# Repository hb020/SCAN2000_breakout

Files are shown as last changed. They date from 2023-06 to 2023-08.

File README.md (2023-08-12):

# SCAN2000_breakout

This repository contains the KiCAD and Freecad project files for a breakout panel for for a Keithley SCAN2000-20 replacement card.

It is a specific breakout board in the sense that it holds the (solid-state) relays inside, lowering the overal electrical noise.

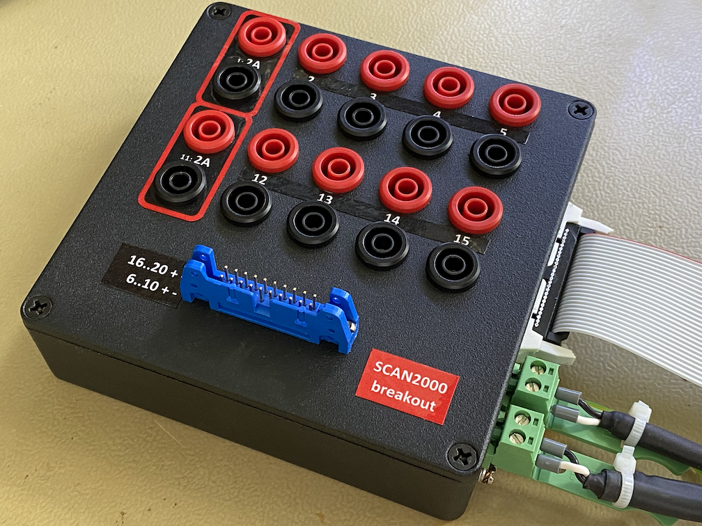
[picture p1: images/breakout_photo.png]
case


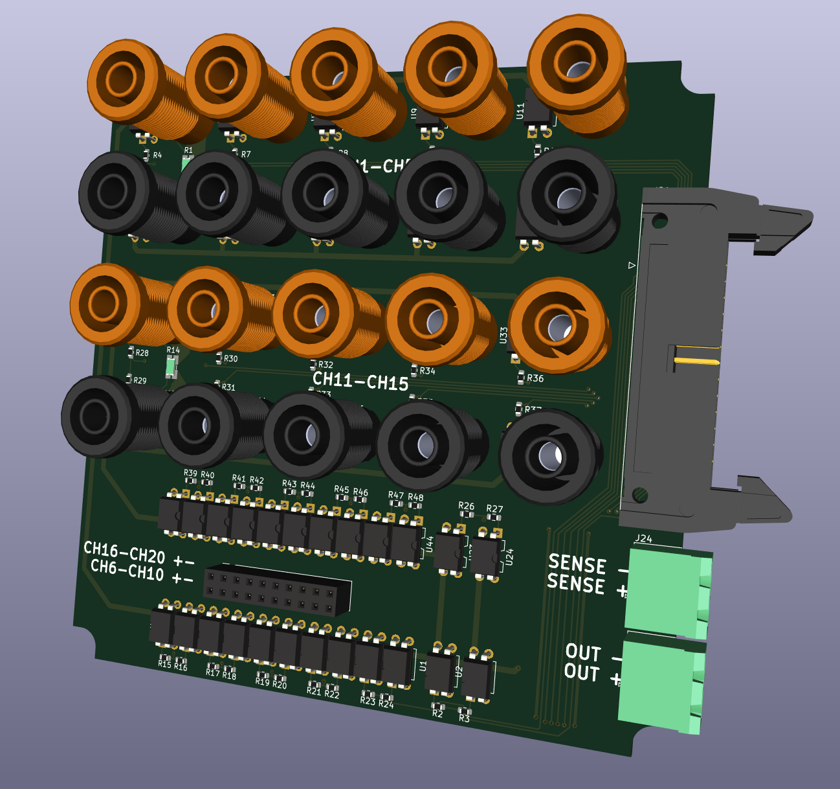
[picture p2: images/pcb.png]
PCB


It is supposed to be matched with the board from [here](https://github.com/hb020/SCAN2000):
SCAN2000_PCB
either directly, either via a small mezzanine driver/ESD suppression board that can be found in the [/SCAN2000_driver](/SCAN2000_driver) directory.
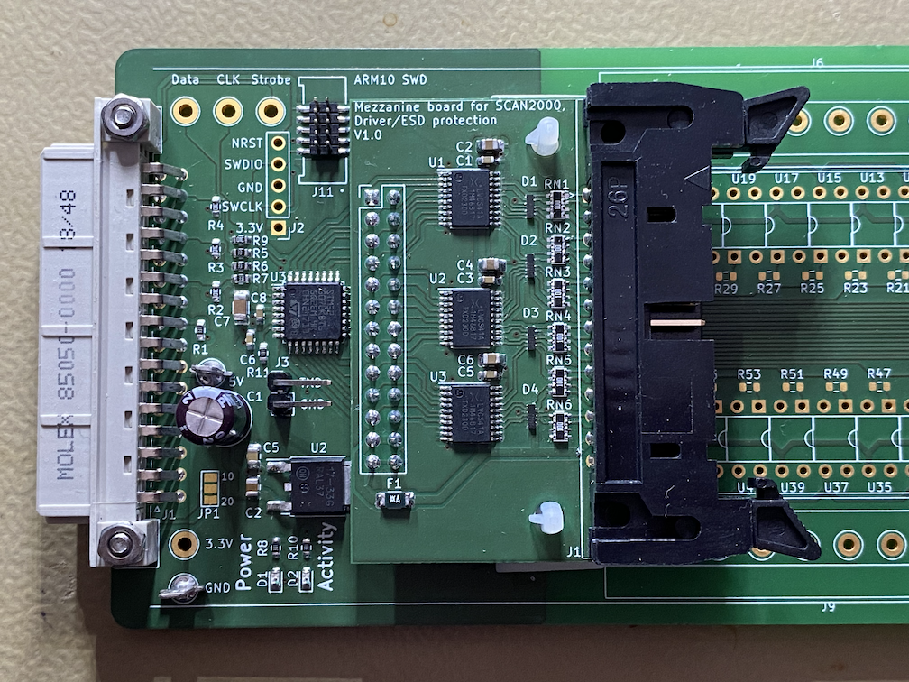
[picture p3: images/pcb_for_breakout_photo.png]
SCAN2000_Mezzanine_PCB


That latter board will give a bit more protection against small electrical mishaps, and will allow a load of up to 24 or 35mA per pin (depending on the chip manufacturer), instead of 15mA, allowing extra leds to be driven.

To facilitate plugging/unplugging from the DMM, I also made a small 4 pin connector board for the back of the DMM. See the [/SCAN2000_rearconn](/SCAN2000_rearconn) directory.

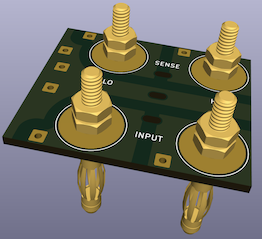
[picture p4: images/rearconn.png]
rearconn


# Functionality

The board provides 20 channels:

* 2 banana inputs meant for current measurements. It uses 100 mOhm kelvin shunts, allowing up to 2A. One could go higher with lower shunt values or larger package sizes. Note that the accuracy in the µA range suffers from the noise and leak currents in the SSR. This means that if you want a higher current handling capacity, you will sacrifice low current accuracy. And the reverse of course. There are 2 inputs like it, so you are free to adjust, and you can always use external shunts.
* 8 banana inputs for voltage measurements or 4W resistance measurements.
* 10 pin header inputs for voltage measurements or 4W resistance measurements.

# Calibration

See the [/scan2000_calibrate](/scan2000_calibrate) directory for the determination of the multiplication factors for the voltage to current conversion on channels 1 and 11. Can be done simpler though.

A sample TSP file is [here](breakoutAmps.tsp). You may want to add that to your autoexec script.

# Production

The case chosen is a Hammond 1590QBK. It is just small enough to fit everything required inside, and not be a space hogger on my desk. It machines well, even on my rather low end CNC:

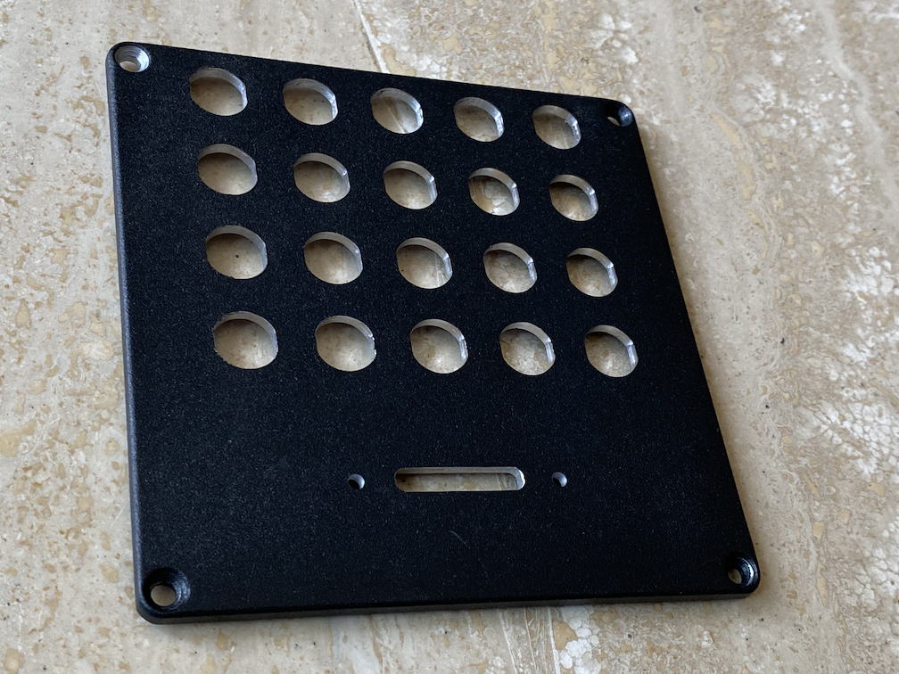
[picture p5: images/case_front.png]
case_front


The Freecad files, the GCode, as well as the front stickers, are in the [/freecad](/freecad) directory.
The paint on it is not completely flat, making sticker adhesion a bit more difficult and making milled text not practical.

The grounding of the case is done through a threaded rivet in the case that is connected to the ground screw on the rear of the DMM via the shielding of the OUT cable.

# TODO

* Integrate the mezzanine board in the SCAN2000 board. But then I should also replace the ESD diodes by a real overvoltage protection. The used diodes are effective against some types of ESD, but get damaged easily with DC currents. And hand soldering them isn't easy.
* Find a black 26 pin flat cable header, the white one I got now hurts the eyes.
* Use nicer connectors than the MSTB 5.08 connectors. The OUT/SENSE cables that I used to connect to the DMM are shielded, making them just a bit stiff, so I had to use MSTB 2,5/ 2-STZ-5,08 connectors that have strain relief. It would be better to move to a regular 4 or 5 pin connector.
* Make a 3D printed case for the rearconn connector. I just applied plastic coating to the PCB, not ideal.

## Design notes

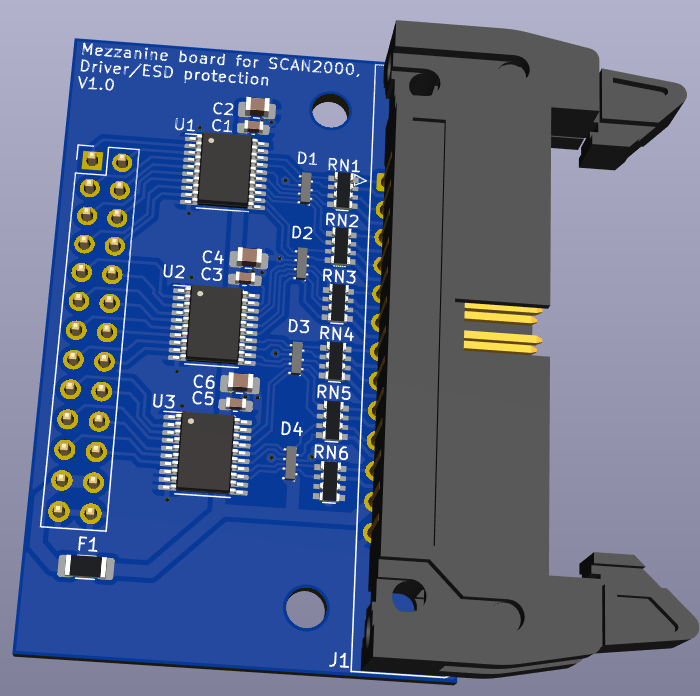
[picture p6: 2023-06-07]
images/mezzanine_pcb.png

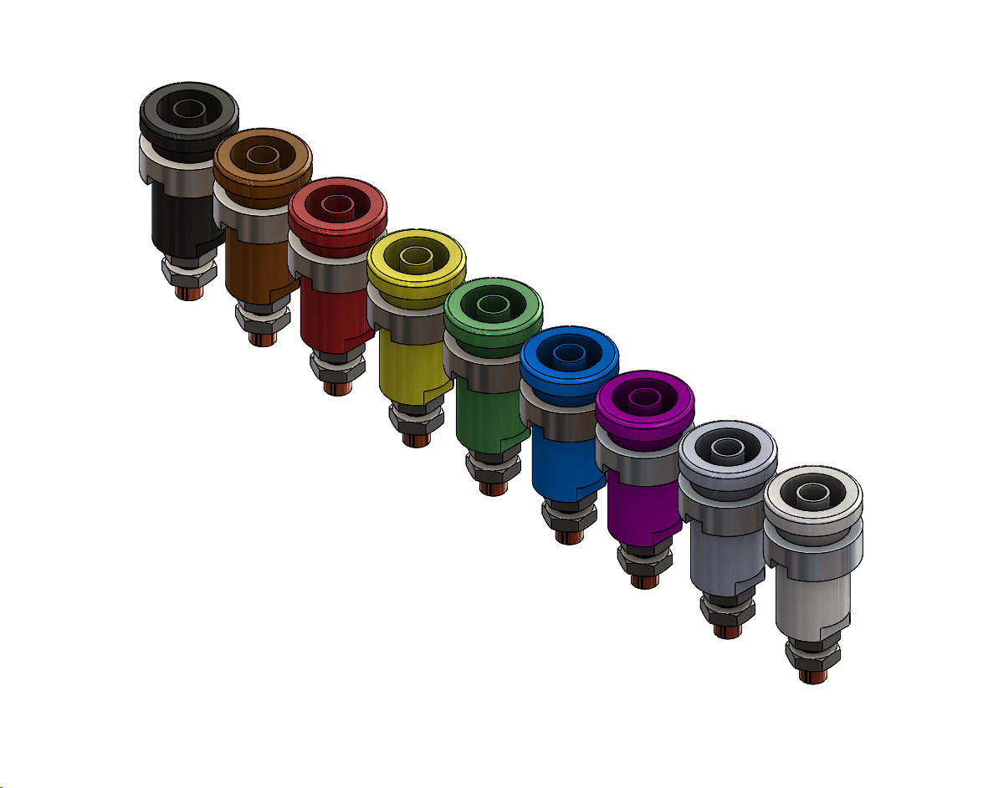
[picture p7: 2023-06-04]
freecad/banana-jack-collection-1.snapshot.1/Clip.jpg

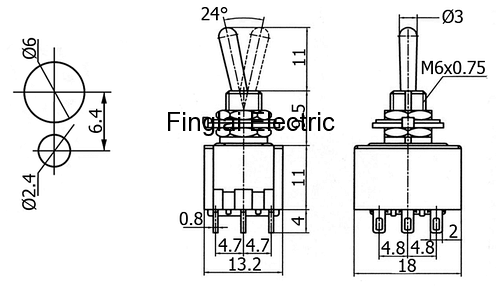
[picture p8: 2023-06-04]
freecad/MTS-303 3PDT Toggle Switch/MTS-303-drawing.png

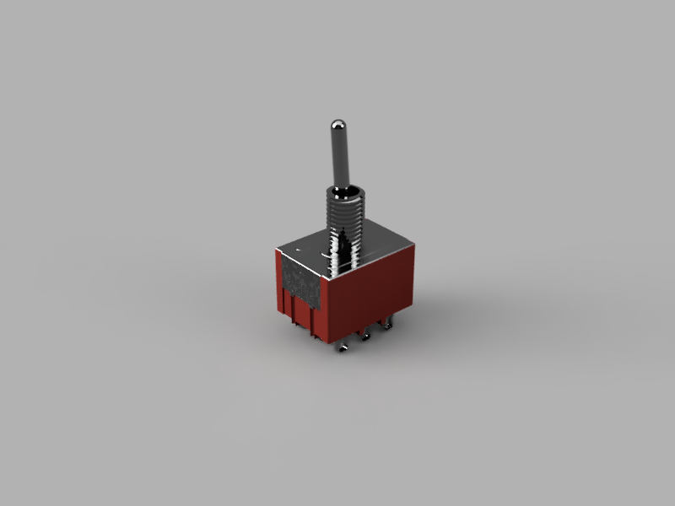
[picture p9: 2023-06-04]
freecad/MTS-303 3PDT Toggle Switch/MTS-303 3PDT Toggle Switch .png

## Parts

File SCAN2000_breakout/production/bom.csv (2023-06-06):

Designator | Footprint | Quantity | Value | LCSC Part #
J1, J11, J13, J15, J17, J19, J3, J5, J7, J9 | CT2908-1 | 10 | Banana socket
J10, J12, J14, J16, J18, J2, J20, J4, J6, J8 | CT2908-0 | 10 | Banana socket
J21 | IDC-Header_2x13_P2.54mm_Latch_Horizontal | 1 | Conn_01x26_HIGHin
J22 | PinSocket_2x10_P2.54mm_Vertical | 1 | Conn_02x10_Odd_Even
J23, J24 | PhoenixContact_MSTBA_2,5_2-G-5,08_1x02_P5.08mm_Horizontal | 2 | Conn_01x02_Pin
R1, R14 | R_Shunt_Ohmite_LVK12_ALT2 | 2 | 0.05
R10, R11, R12, R13, R15, R16, R17, R18, R19, R2, R20, R21, R22, R23, R24, R26, R27, R28, R29, R3, R30, R31, R32, R33, R34, R35, R36, R37, R39, R4, R40, R41, R42, R43, R44, R45, R46, R47, R48, R5, R6, R7, R8, R9 | 0603 | 44 | 330R
U1, U10, U11, U12, U13, U14, U15, U16, U17, U18, U19, U2, U20, U21, U22, U23, U24, U25, U26, U27, U28, U29, U3, U30, U31, U32, U33, U34, U35, U36, U37, U38, U39, U4, U40, U41, U42, U43, U44, U5, U6, U7, U8, U9 | DIP-4_W7.62mm | 44 | TLP3558A

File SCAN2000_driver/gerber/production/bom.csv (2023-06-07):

Designator | Footprint | Quantity | Value | LCSC Part #
C1, C3, C5 | 0603 | 3 | 100nF
C2, C4, C6 | 0805 | 3 | 1uF
D1, D2, D3, D4 | RCLAMP3346PQTNT | 4 | RCLAMP3346P.TNT
F1 | 1206 | 1 | Polyfuse 100mA
H1, H2 | MountingHole_3.2mm_M3_DIN965 | 2 | MountingHole
J1 | IDC-Header_2x13_P2.54mm_Latch_Horizontal | 1 | IDC-Header_2x13
J2 | PinHeader_2x13_P2.54mm_Vertical | 1 | Header 2x13
RN1, RN2, RN3, RN4, RN5, RN6 | R_Array_Convex_4x0603 | 6 | 4x10R
U1, U2, U3 | TSSOP-20_4.4x6.5mm_P0.65mm | 3 | 74LVC541AP

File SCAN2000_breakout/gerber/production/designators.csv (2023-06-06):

J1:1
J10:1
J11:1
J12:1
J13:1
J14:1
J15:1
J16:1
J17:1
J18:1
J19:1
J2:1
J20:1
J21:1
J22:1
J23:1
J24:1
J3:1
J4:1
J5:1
J6:1
J7:1
J8:1
J9:1
R1:1
R10:1
R11:1
R12:1
R13:1
R14:1
R15:1
R16:1
R17:1
R18:1
R19:1
R2:1
R20:1
R21:1
R22:1
R23:1
R24:1
R26:1
R27:1
R28:1
R29:1
R3:1
R30:1
R31:1
R32:1
R33:1
R34:1
R35:1
R36:1
R37:1
R39:1
R4:1
R40:1
R41:1
R42:1
R43:1
R44:1
R45:1
R46:1
R47:1
R48:1
R5:1
R6:1
R7:1
R8:1
R9:1
U1:1
U10:1
U11:1
U12:1
U13:1
U14:1
U15:1
U16:1
U17:1
U18:1
U19:1
U2:1
U20:1
U21:1
U22:1
U23:1
U24:1
U25:1
U26:1
U27:1
U28:1
U29:1
U3:1
U30:1
U31:1
U32:1
U33:1
U34:1
U35:1
U36:1
U37:1
U38:1
U39:1
U4:1
U40:1
U41:1
U42:1
U43:1
U44:1
U5:1
U6:1
U7:1
U8:1
U9:1

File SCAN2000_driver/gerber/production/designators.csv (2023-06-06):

C1:1
C2:1
C3:1
C4:1
C5:1
C6:1
D1:1
D2:1
D3:1
D4:1
F1:1
H1:1
H2:1
J1:1
J2:1
RN1:1
RN2:1
RN3:1
RN4:1
RN5:1
RN6:1
U1:1
U2:1
U3:1

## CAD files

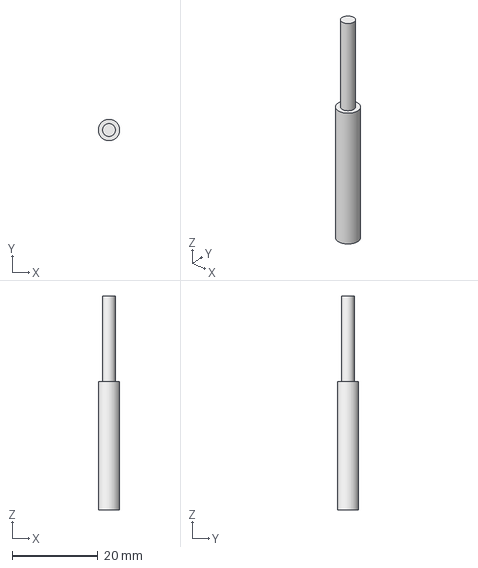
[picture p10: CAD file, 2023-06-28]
freecad/lid_cutout.FCStd
5.00 x 5.00 x 50.0 mm

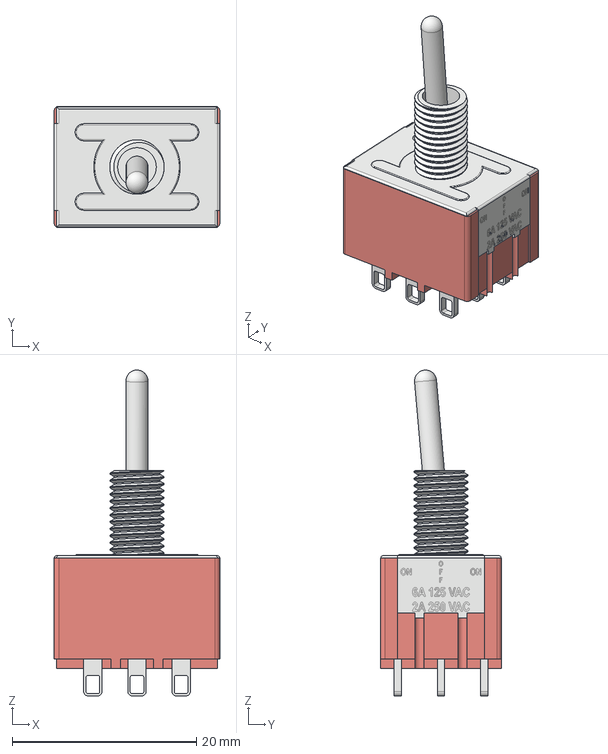
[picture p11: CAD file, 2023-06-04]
freecad/MTS-303 3PDT Toggle Switch/MTS-303 3PDT Toggle Switch.step
18.0 x 13.2 x 35.4 mm

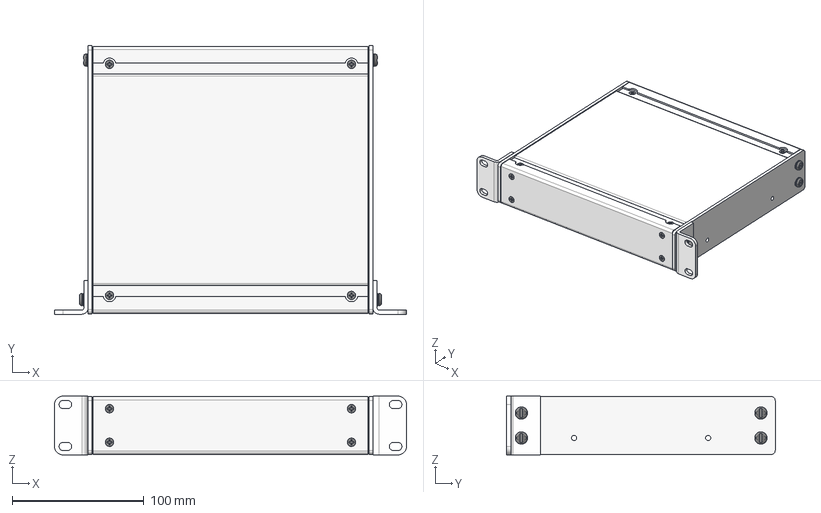
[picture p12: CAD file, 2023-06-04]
freecad/RMCS9018BK1/RMCS9018.stp
266.7 x 203.4 x 44.5 mm
COM53879 x 2
COM53875-1 x 2
COM53876-1 x 2
COM53878-1 x 2
SCS19498 x 8
SCS19535 x 16
COM54125 x 4
NTS16847 x 8
NTS16752 x 16

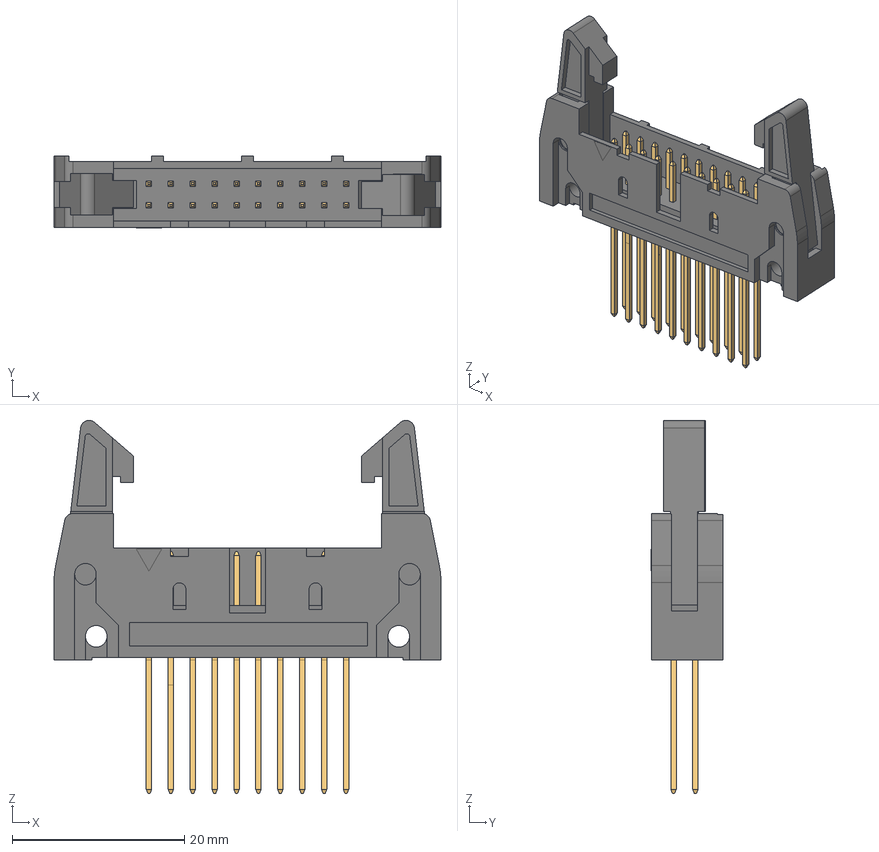
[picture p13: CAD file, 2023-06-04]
SCAN2000_breakout/project_specific_libs/CWN-370-20-xxxx.step
44.9 x 8.31 x 43.3 mm
6120xx22x21_LEVIER_LONG x 2
6120xx21621_PIN x 20
6120xx21621_PIN020
6120xx21621_PIN021
6120xx21621_PIN022
6120xx21621_PIN023
6120xx21621_PIN024
6120xx21621_PIN025
6120xx21621_PIN026
6120xx21621_PIN027
6120xx21621_PIN028
6120xx21621_PIN029
6120xx21621_PIN030
6120xx21621_PIN031
6120xx21621_PIN032
6120xx21621_PIN033
6120xx21621_PIN034
6120xx21621_PIN035
6120xx21621_PIN036
6120xx21621_PIN037
6120xx21621_PIN038
6120xx21621_PIN039

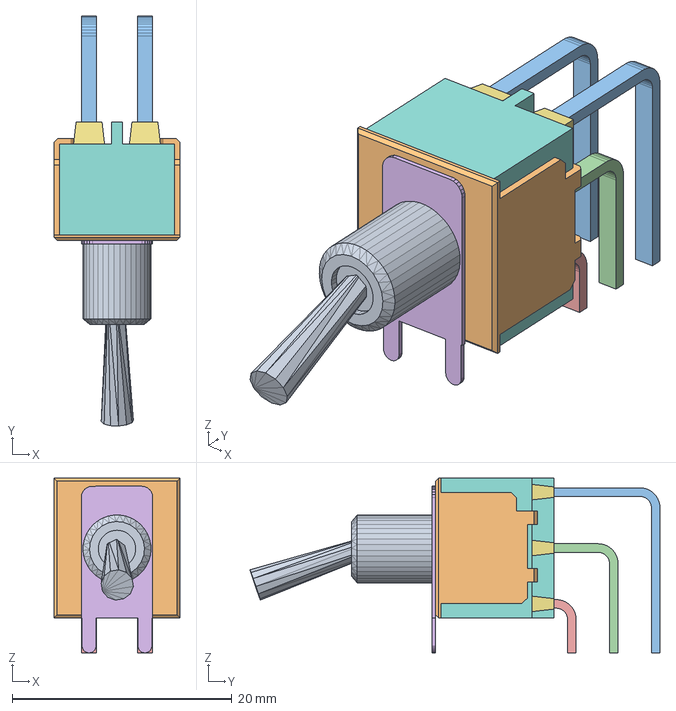
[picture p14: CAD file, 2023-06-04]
freecad/7201MD9AV2BE.stp
11.4 x 37.3 x 15.9 mm

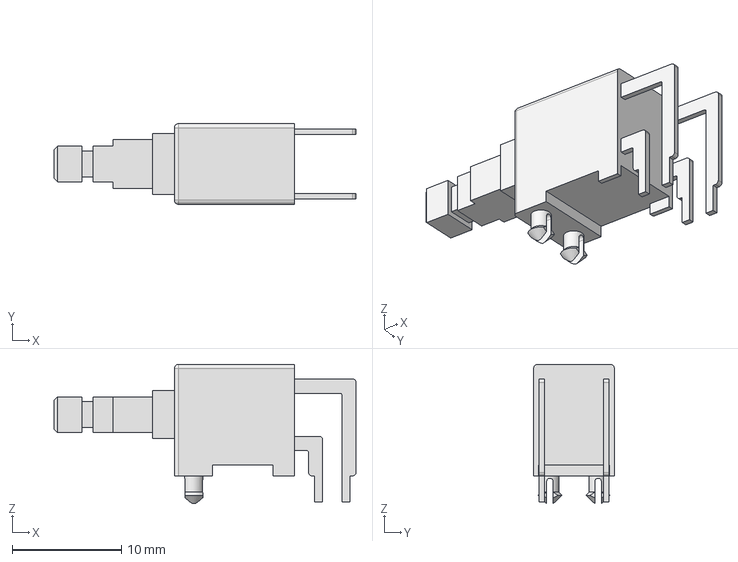
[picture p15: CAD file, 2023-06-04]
SCAN2000_breakout/project_specific_libs/PB400EEQX.step
27.6 x 7.40 x 12.8 mm

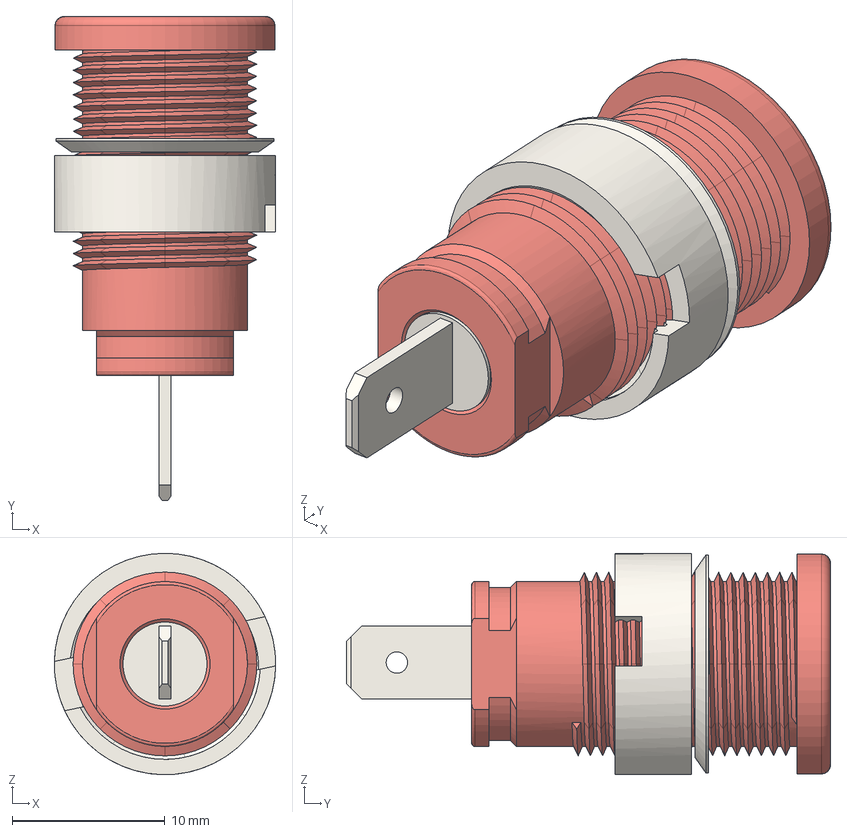
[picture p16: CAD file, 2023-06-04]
freecad/Banana Plug 4mm Black CT2238 v1.FCStd
14.5 x 31.7 x 14.5 mm
User Library-Stor banan_Stor banan bricka
User Library-Stor banan_Stor banan mutter
User Library-Stor banan_Stor banan
User Library-Stor banan_Stor banan koppar

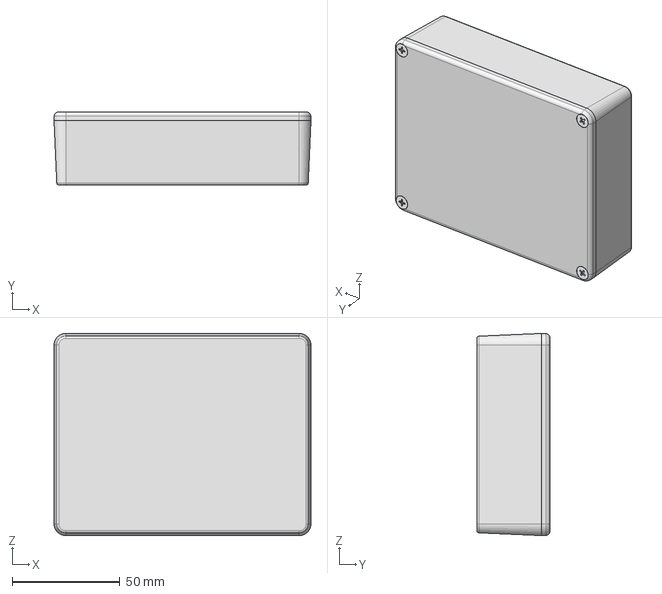
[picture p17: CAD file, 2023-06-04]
freecad/1590BBBK.stp
119.5 x 34.0 x 94.0 mm

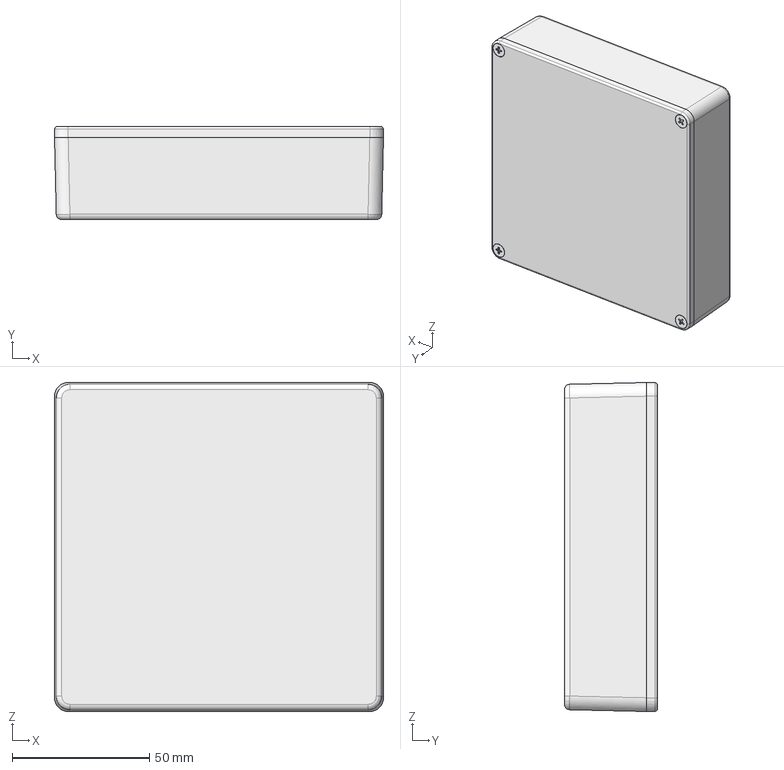
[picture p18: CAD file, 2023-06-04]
freecad/1590Q.stp
120.0 x 34.0 x 120.0 mm

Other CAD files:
freecad/banana-jack-collection-1.snapshot.1/Cal Test CT2236-6.SLDPRT
freecad/banana-jack-collection-1.snapshot.1/Cal Test CT2236-9.SLDPRT
freecad/banana-jack-collection-1.snapshot.1/Cal Test CT2236-1.SLDPRT
freecad/banana-jack-collection-1.snapshot.1/Cal Test CT2236-5.SLDPRT
freecad/Banana Plug 4mm Red CT2238 v1.step
freecad/banana-jack-collection-1.snapshot.1/Cal Test CT2236-0.SLDPRT
freecad/banana-jack-collection-1.snapshot.1/Cal Test CT2236-7.SLDPRT
freecad/banana-jack-collection-1.snapshot.1/Cal Test CT2236-2.SLDPRT
SCAN2000_breakout/project_specific_libs/61202022821_Download_STP_61202022821_rev1.stp
SCAN2000_breakout/project_specific_libs/61202622921.stp
SCAN2000_breakout/project_specific_libs/71922_y26_asm.stp
SCAN2000_rearconn/project_specific_libs/72918.stp
freecad/1457L1201EBK.stp
freecad/1457L1601EBK.stp
freecad/1590BB2BK.stp
freecad/1590BBSBK.stp
freecad/20pinheader.FCStd
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

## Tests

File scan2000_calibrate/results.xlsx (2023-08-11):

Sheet: synced_test_NPLC10_no_AutoZ
nr | set | actual1 | actual11 | ch1 | ch11 | avg_actual | abs_actual | m_ch1 | m_ch11 | ch_range | curr_range | calc1 | calc11 | err1 % | err11 % | abs_err1 ppm | abs_err11 |  | ch1 | ch11
0 | -2 | -1.99992357 | -1.99986388 | -0.1998978 | -0.2001775 | -1.99989372 | 1.99989372 | 10.00473027 | 9.99045287 | 1 | 3 | -2.001579271 | -2.0017792 | 0.08% | 0.10% | 827.8823375 | 957.7251828 | m | 10.013 | 10.000
1 | -1.96256527 | -1.96245053 | -1.9624384 | -0.1961739 | -0.1964449 | -1.96244446 | 1.96244446 | 10.00362704 | 9.98976507 | 1 | 3 | -1.964291861 | -1.9644532 | 0.09% | 0.10% | 938.2813334 | 1026.681908 | b | -2.6e-06 | -4.2e-06 | <-- the leak currents of the optos show their influence in the lower current range.
2 | -1.86910978 | -1.86884727 | -1.86884828 | -0.1868112 | -0.1870678 | -1.86884777 | 1.86884777 | 10.0039359 | 9.99021895 | 1 | 3 | -1.870543146 | -1.8706822 | 0.09% | 0.10% | 907.4447266 | 981.3102645 | err ppm | 44597.5048 | 46130.29793
3 | -1.78010455 | -1.77938612 | -1.77938313 | -0.1778588 | -0.1781009 | -1.77938463 | 1.77938463 | 10.00448738 | 9.99087107 | 1 | 3 | -1.780902764 | -1.7810132 | 0.09% | 0.09% | 852.3413682 | 916.0871386
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

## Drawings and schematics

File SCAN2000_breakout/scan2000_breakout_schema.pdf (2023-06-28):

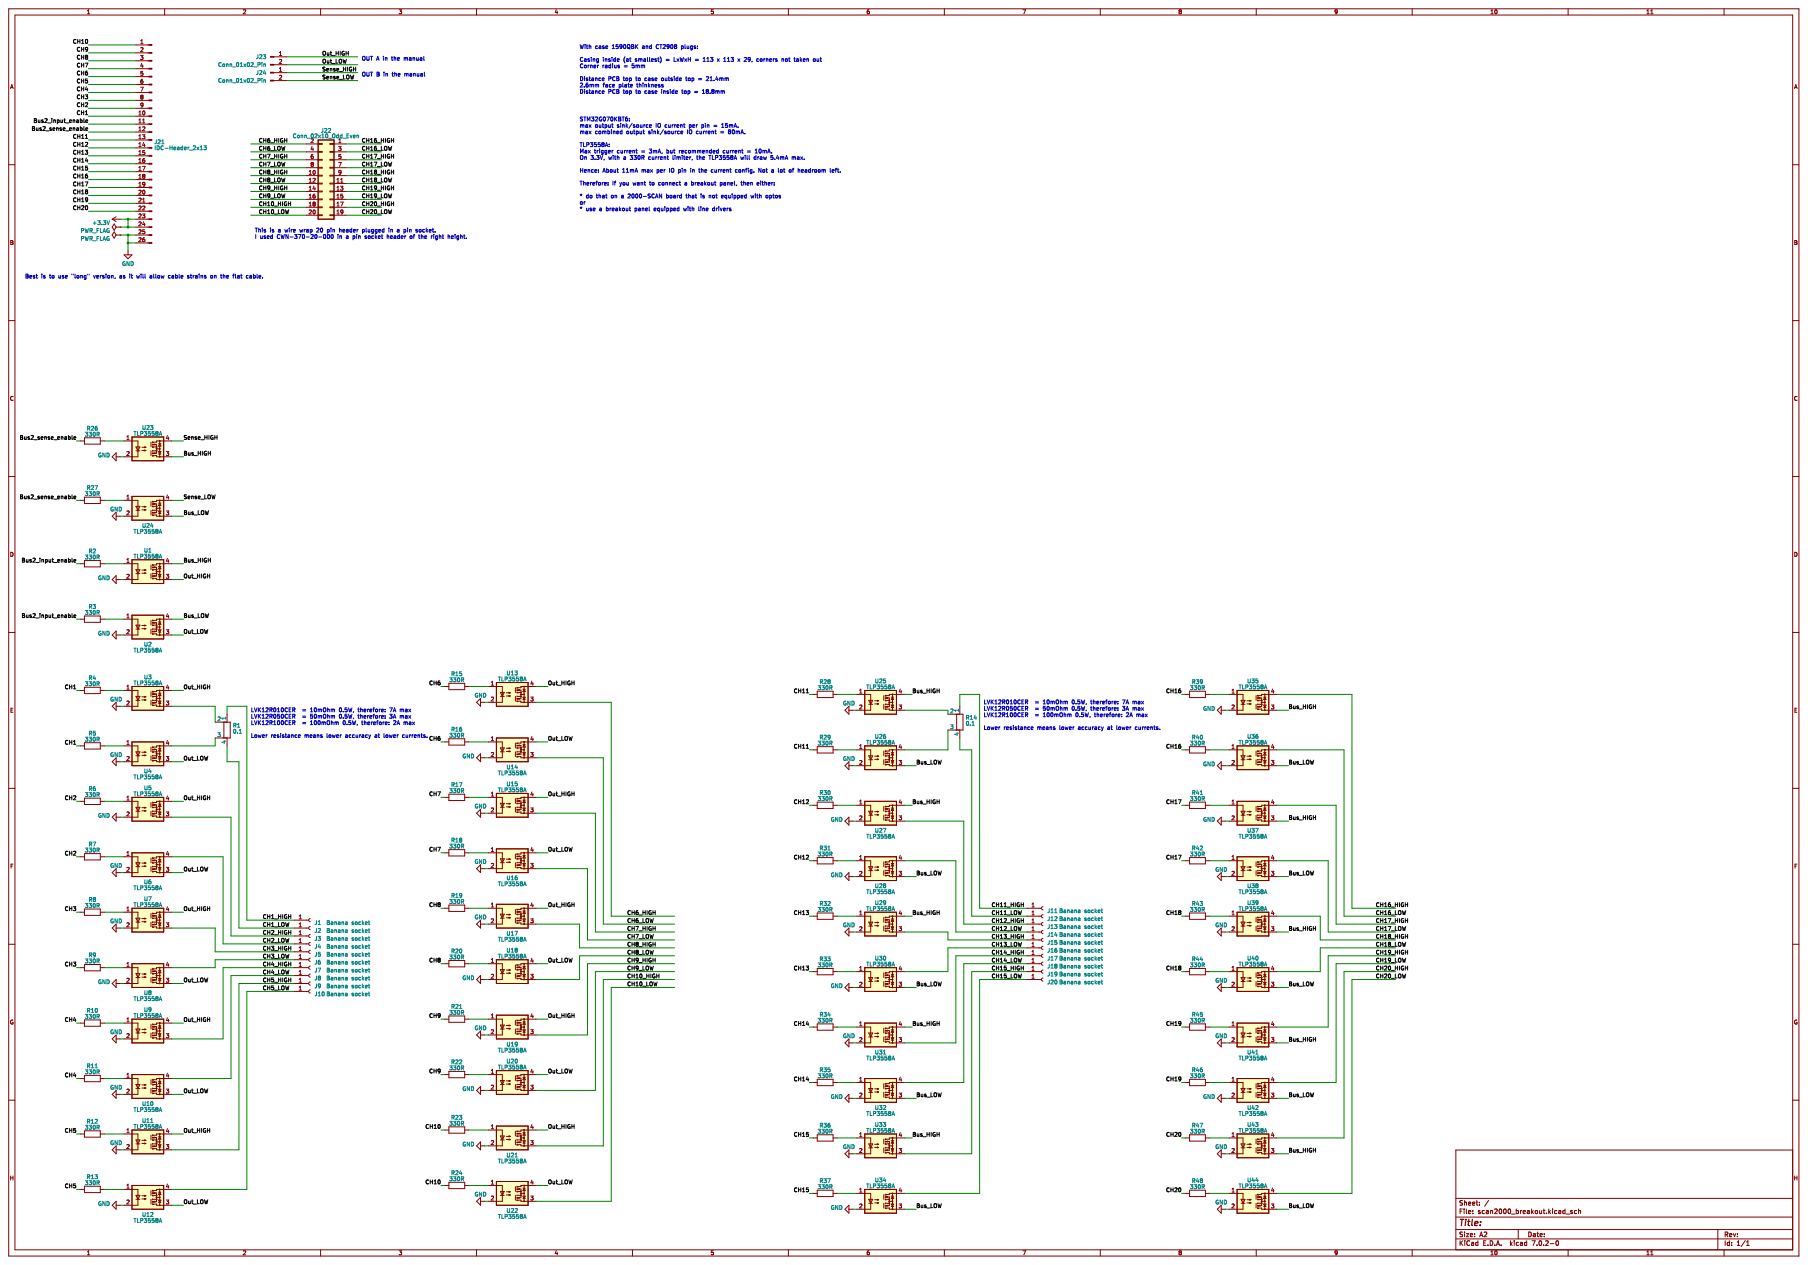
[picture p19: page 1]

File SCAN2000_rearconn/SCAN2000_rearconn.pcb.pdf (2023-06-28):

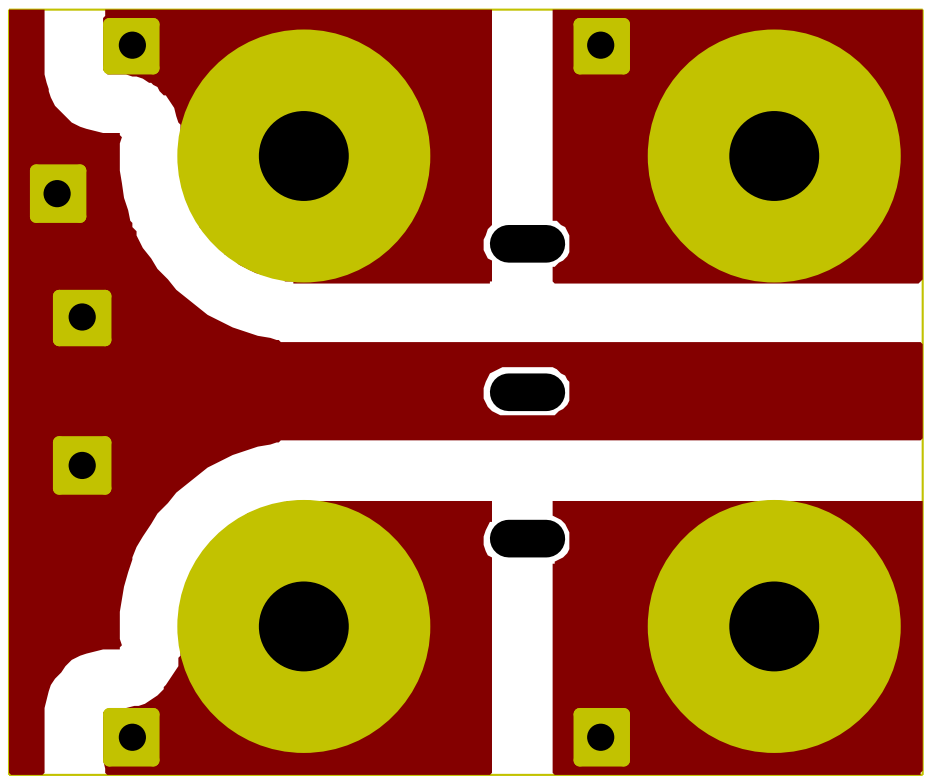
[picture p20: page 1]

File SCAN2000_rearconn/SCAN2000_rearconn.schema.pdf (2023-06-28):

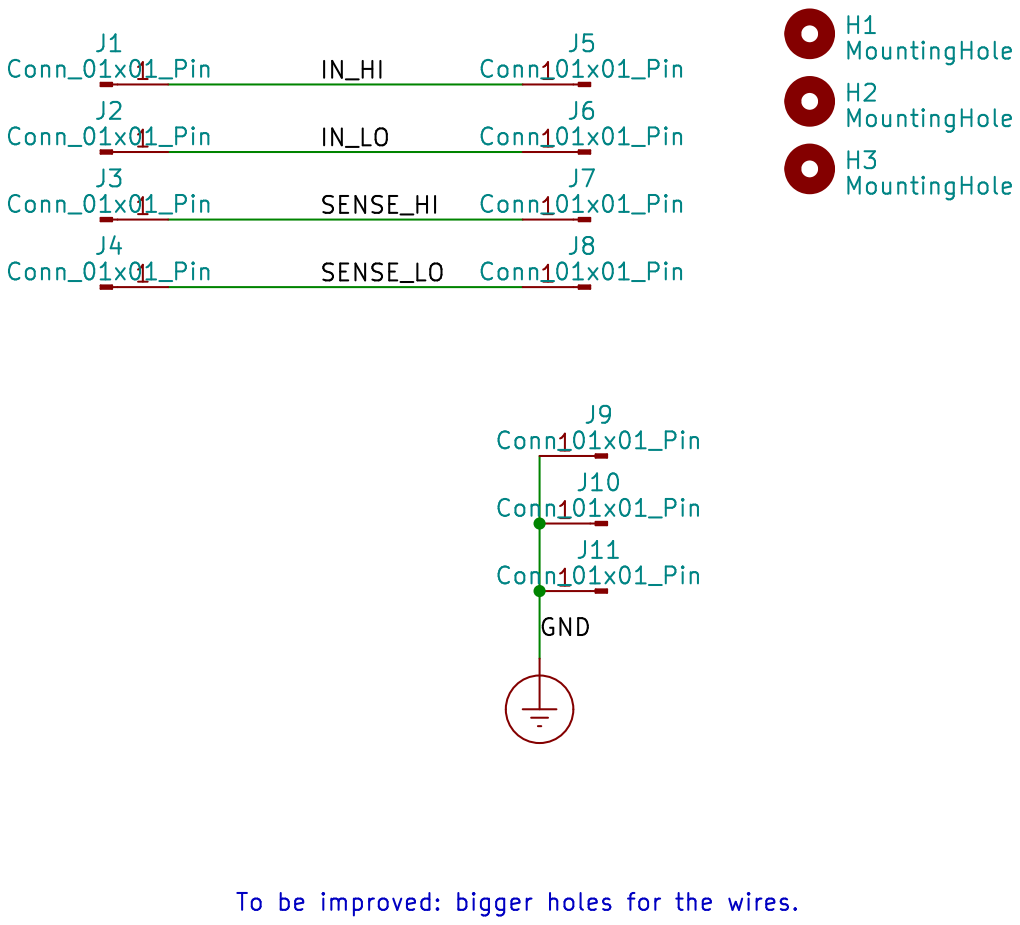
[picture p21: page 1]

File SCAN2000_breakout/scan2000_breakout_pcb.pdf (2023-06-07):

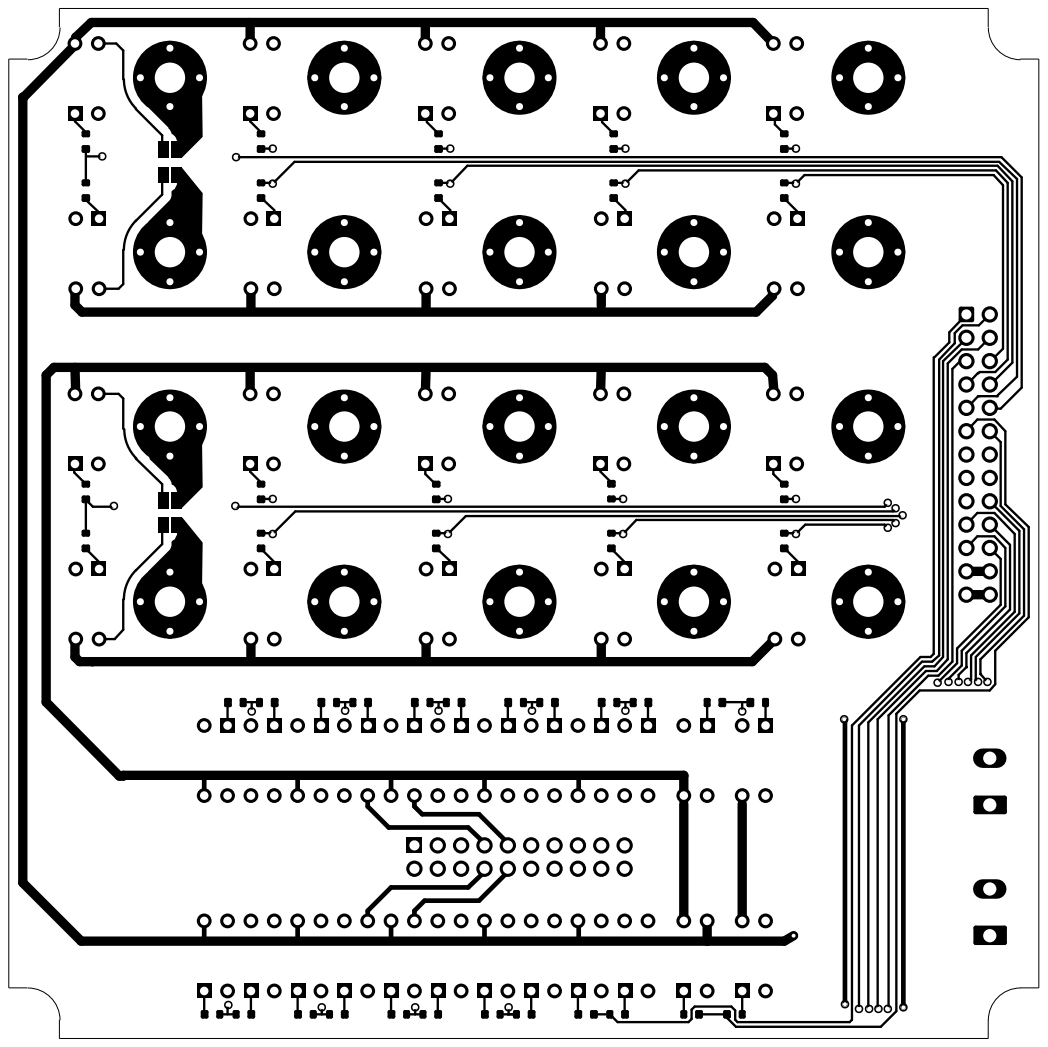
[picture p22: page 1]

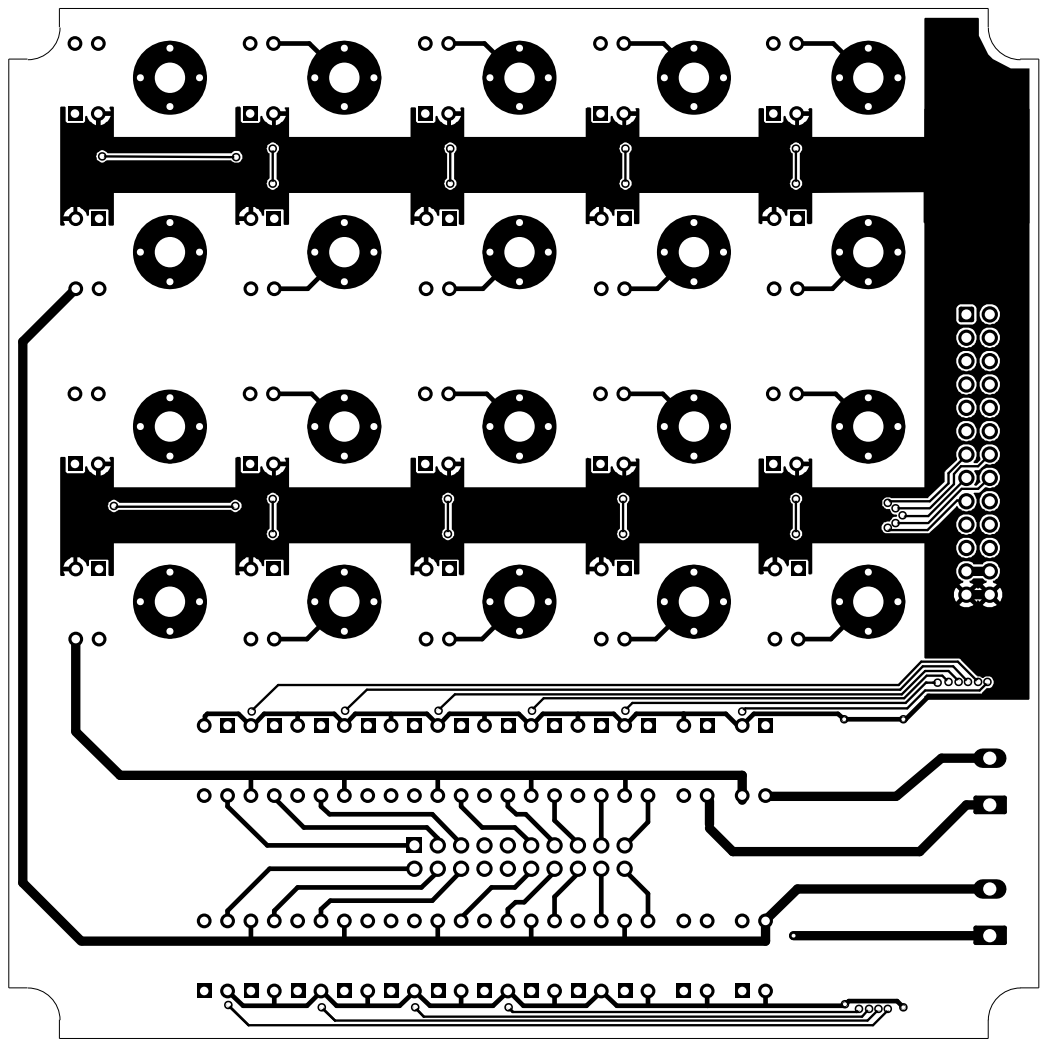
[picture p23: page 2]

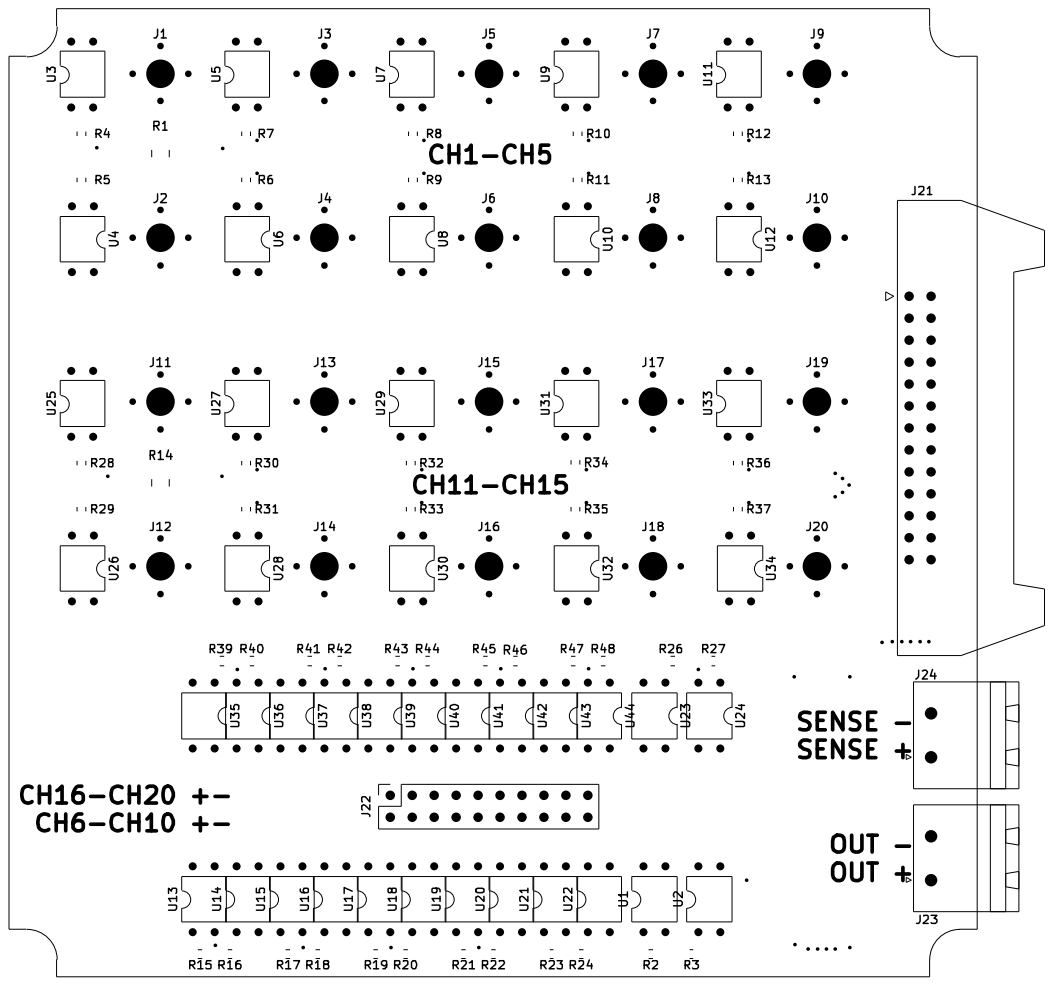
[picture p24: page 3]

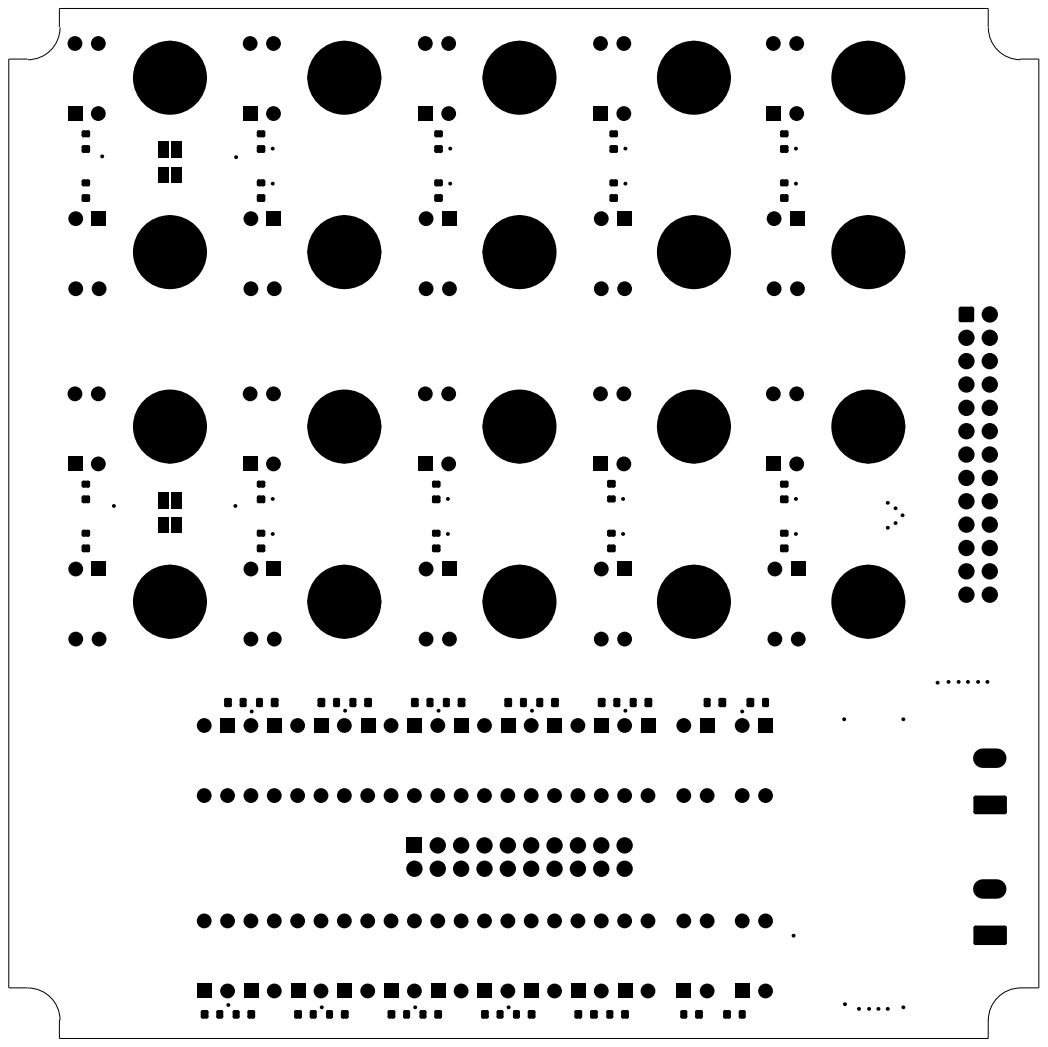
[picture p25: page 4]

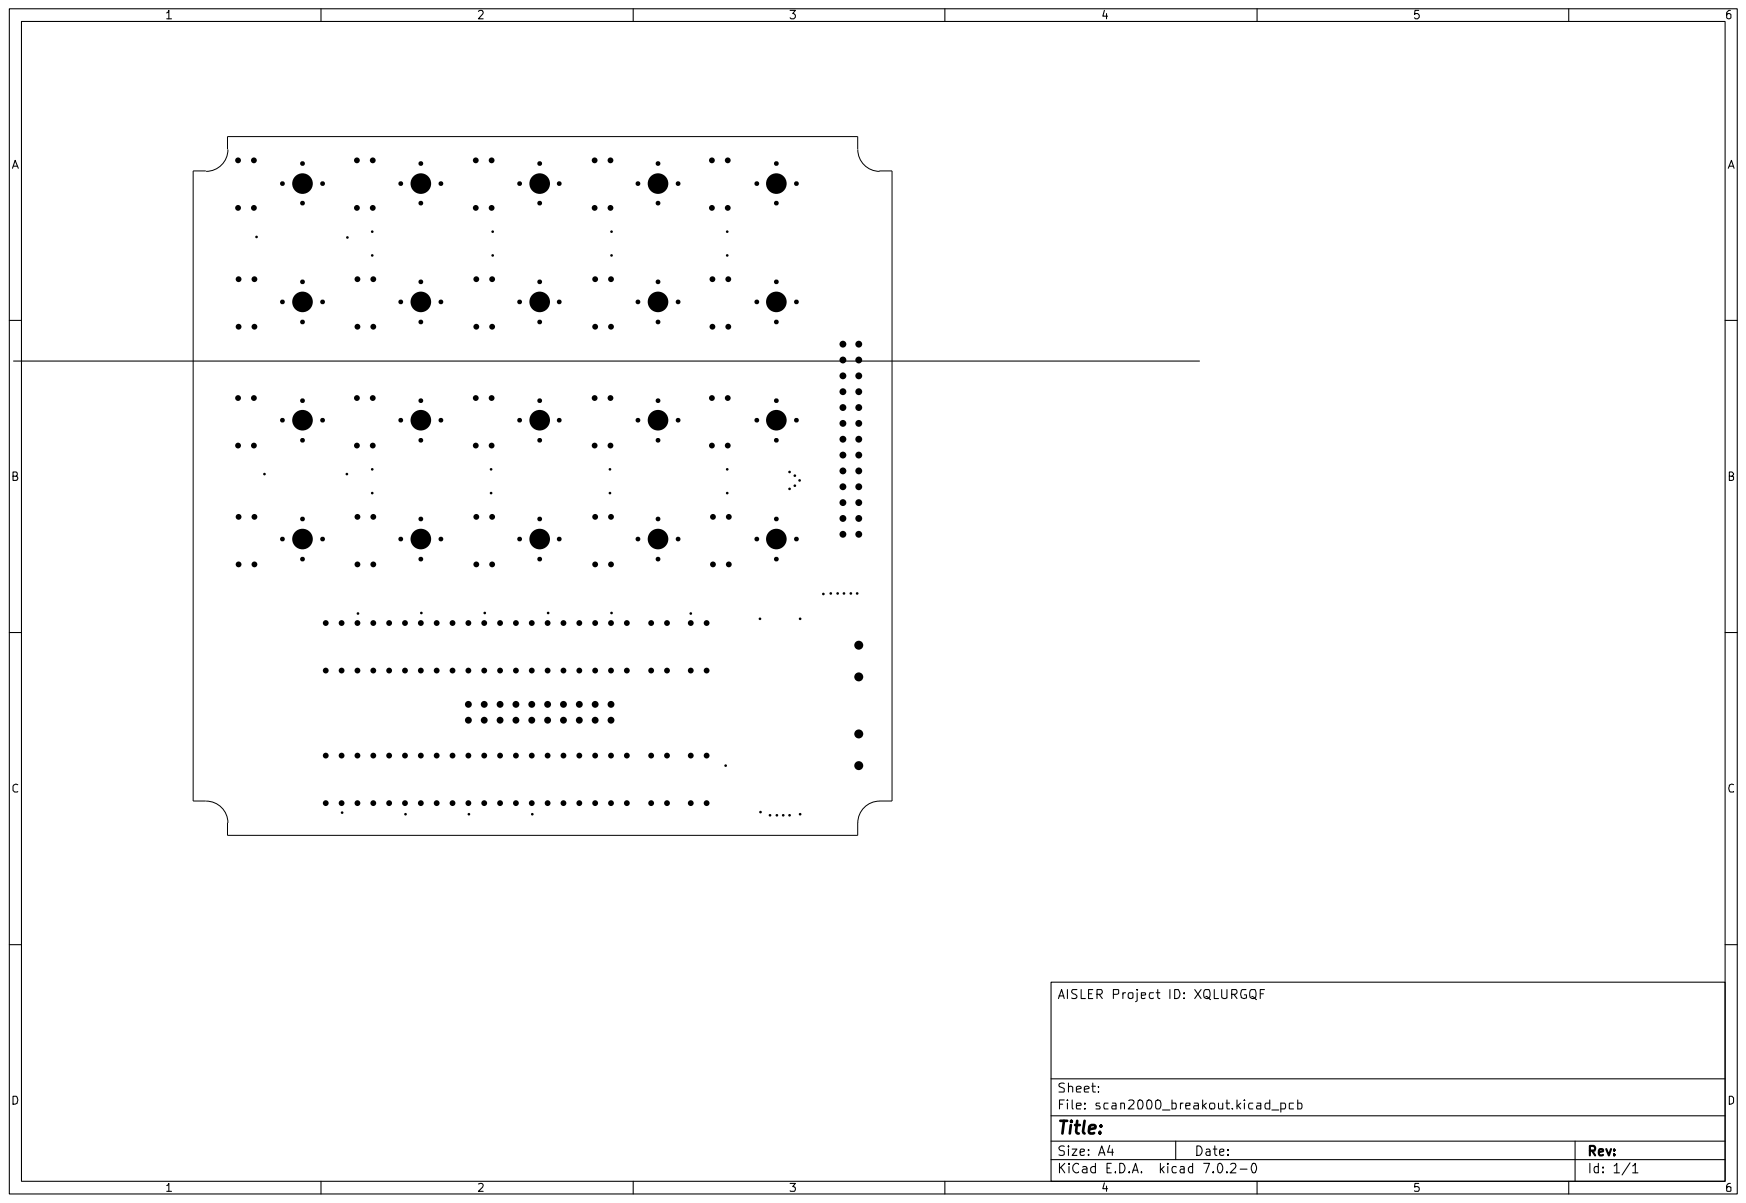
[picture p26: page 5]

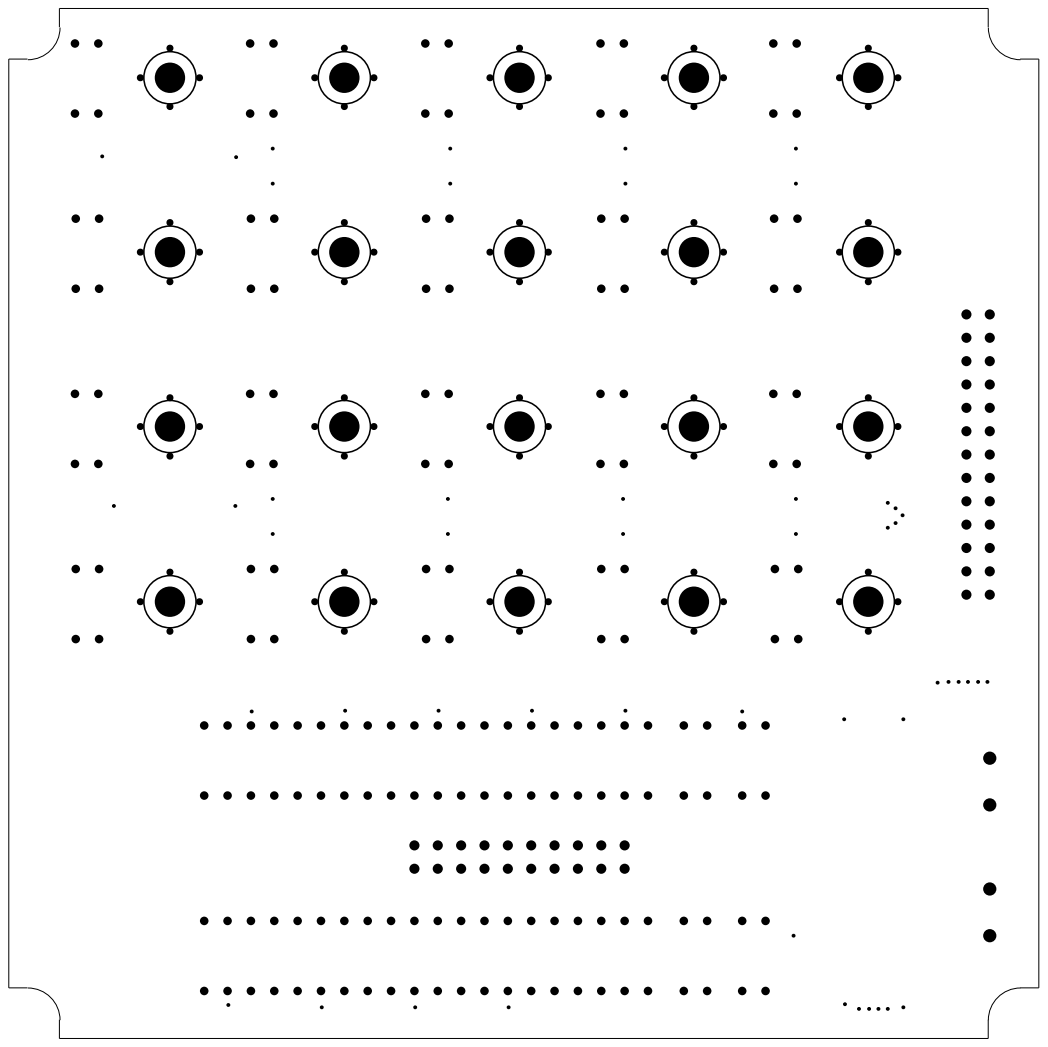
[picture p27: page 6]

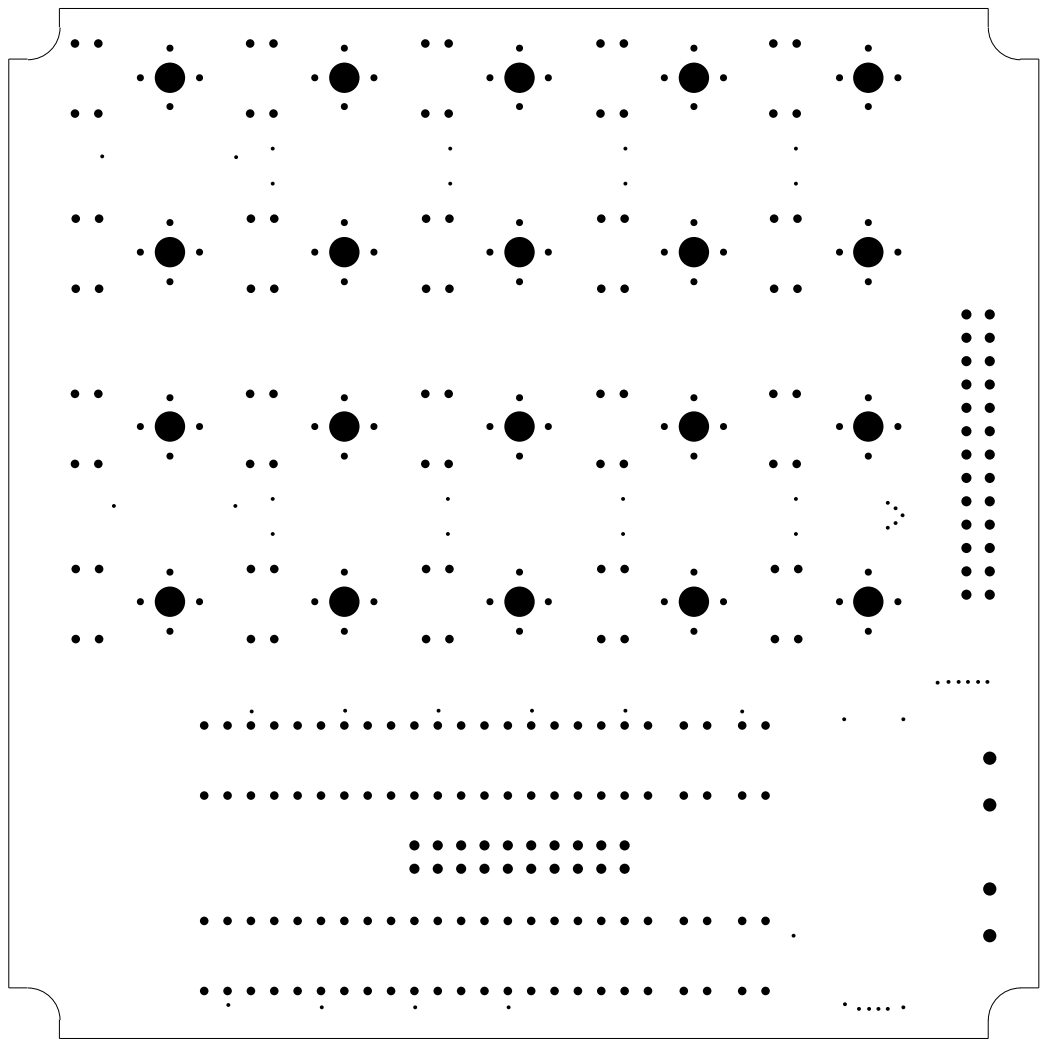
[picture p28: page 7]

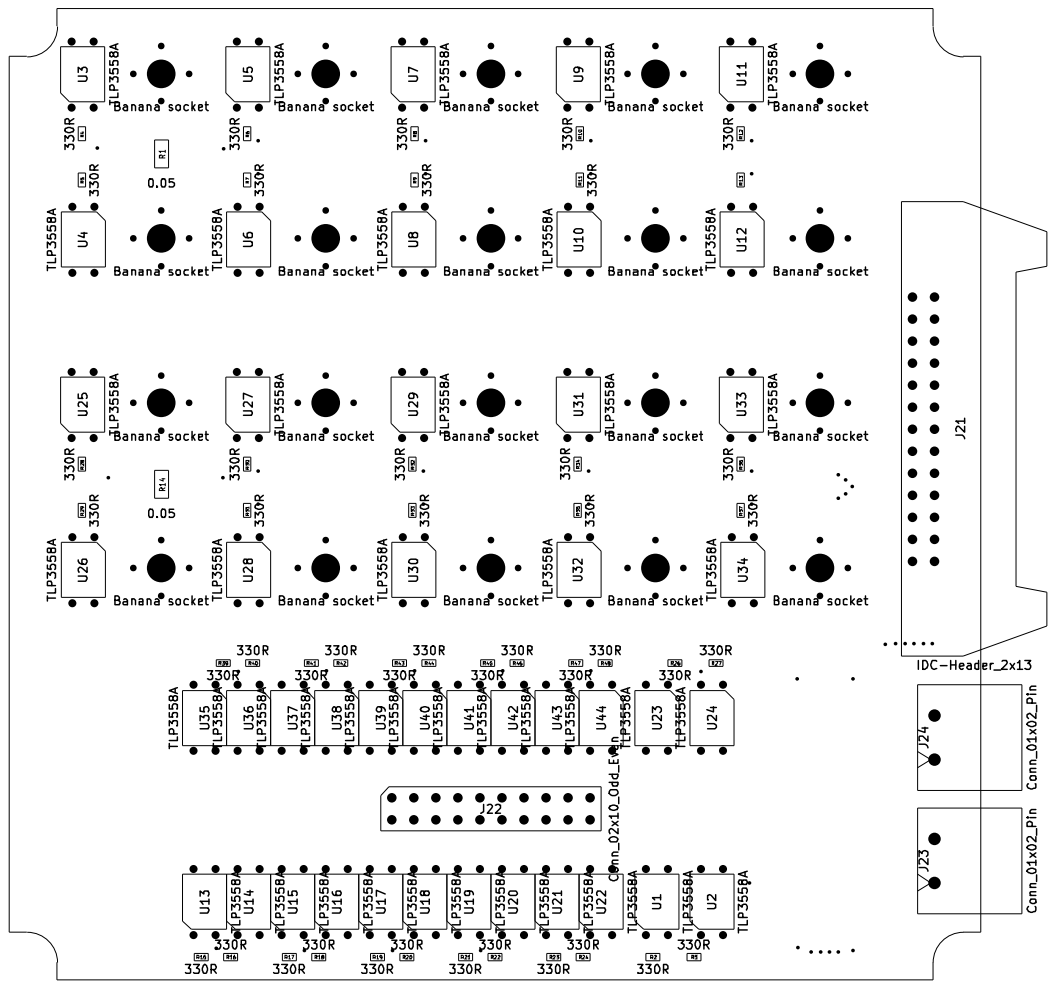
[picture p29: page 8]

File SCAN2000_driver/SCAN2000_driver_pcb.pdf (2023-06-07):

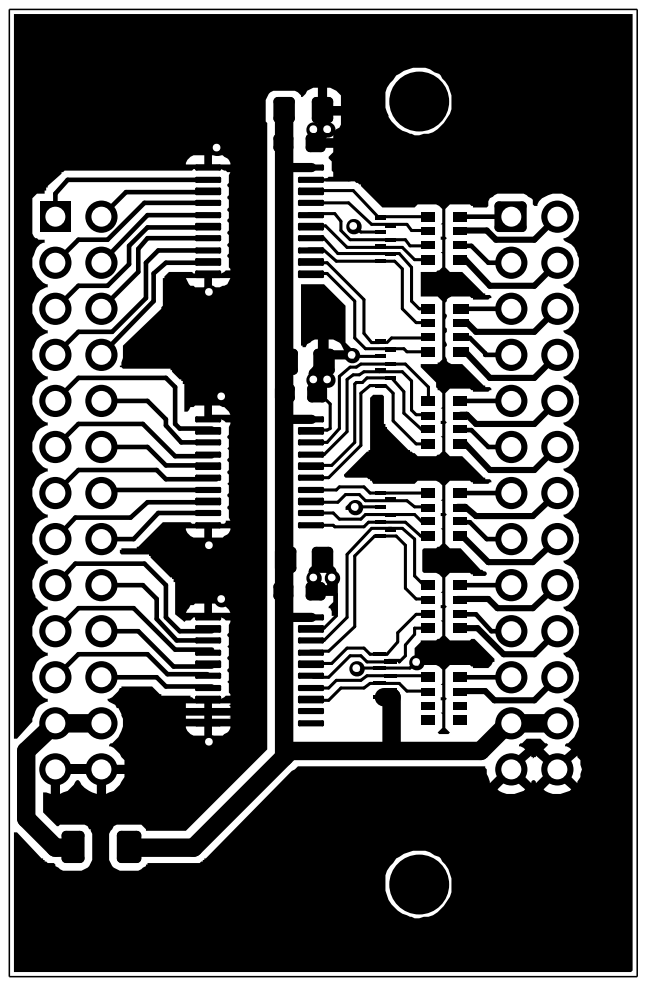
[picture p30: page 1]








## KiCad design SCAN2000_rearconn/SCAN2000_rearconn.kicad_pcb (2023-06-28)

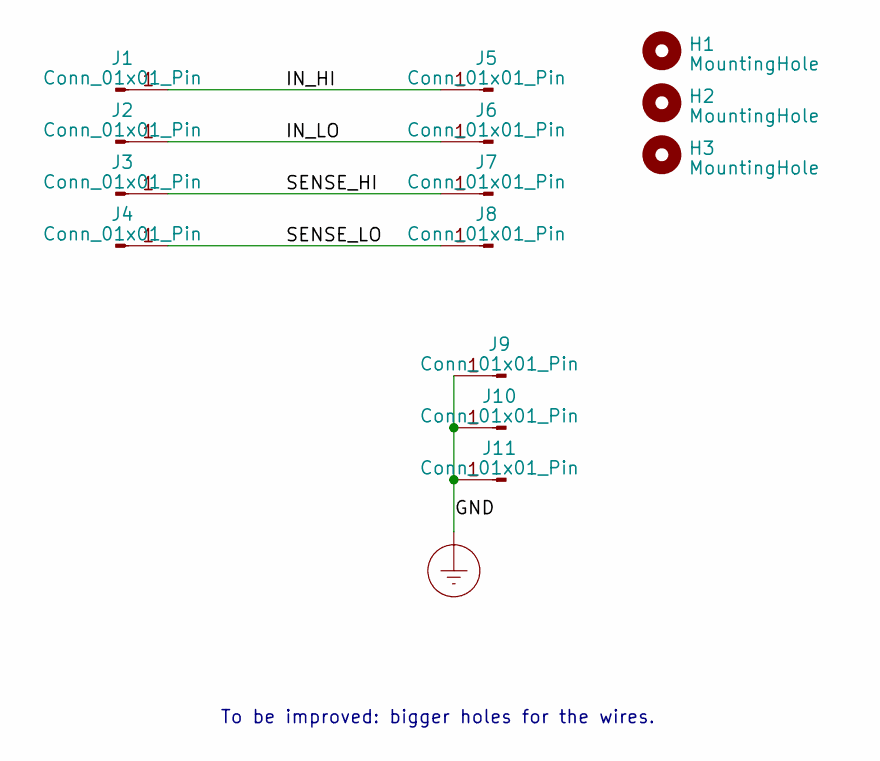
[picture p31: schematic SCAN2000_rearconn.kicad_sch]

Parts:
H1, H2, H3: MountingHole; tiewrap_hole
J1, J2, J3, J4: Conn_01x01_Pin; Banana_Jack_1Pin
J5, J6, J7, J8, J9, J10, J11: Conn_01x01_Pin; SolderWire-0.5sqmm_1x01_D0.9mm_OD2.3mm

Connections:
/IN_HI: J1.1, J5.1
/IN_LO: J2.1, J6.1
/SENSE_HI: J3.1, J7.1
/SENSE_LO: J4.1, J8.1
Earth_Protective: J9.1, J10.1, J11.1

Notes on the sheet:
To be improved: bigger holes for the wires.

Board: 2 copper layers, 14 parts (0 on the bottom side), 5 nets, no tracks yet.

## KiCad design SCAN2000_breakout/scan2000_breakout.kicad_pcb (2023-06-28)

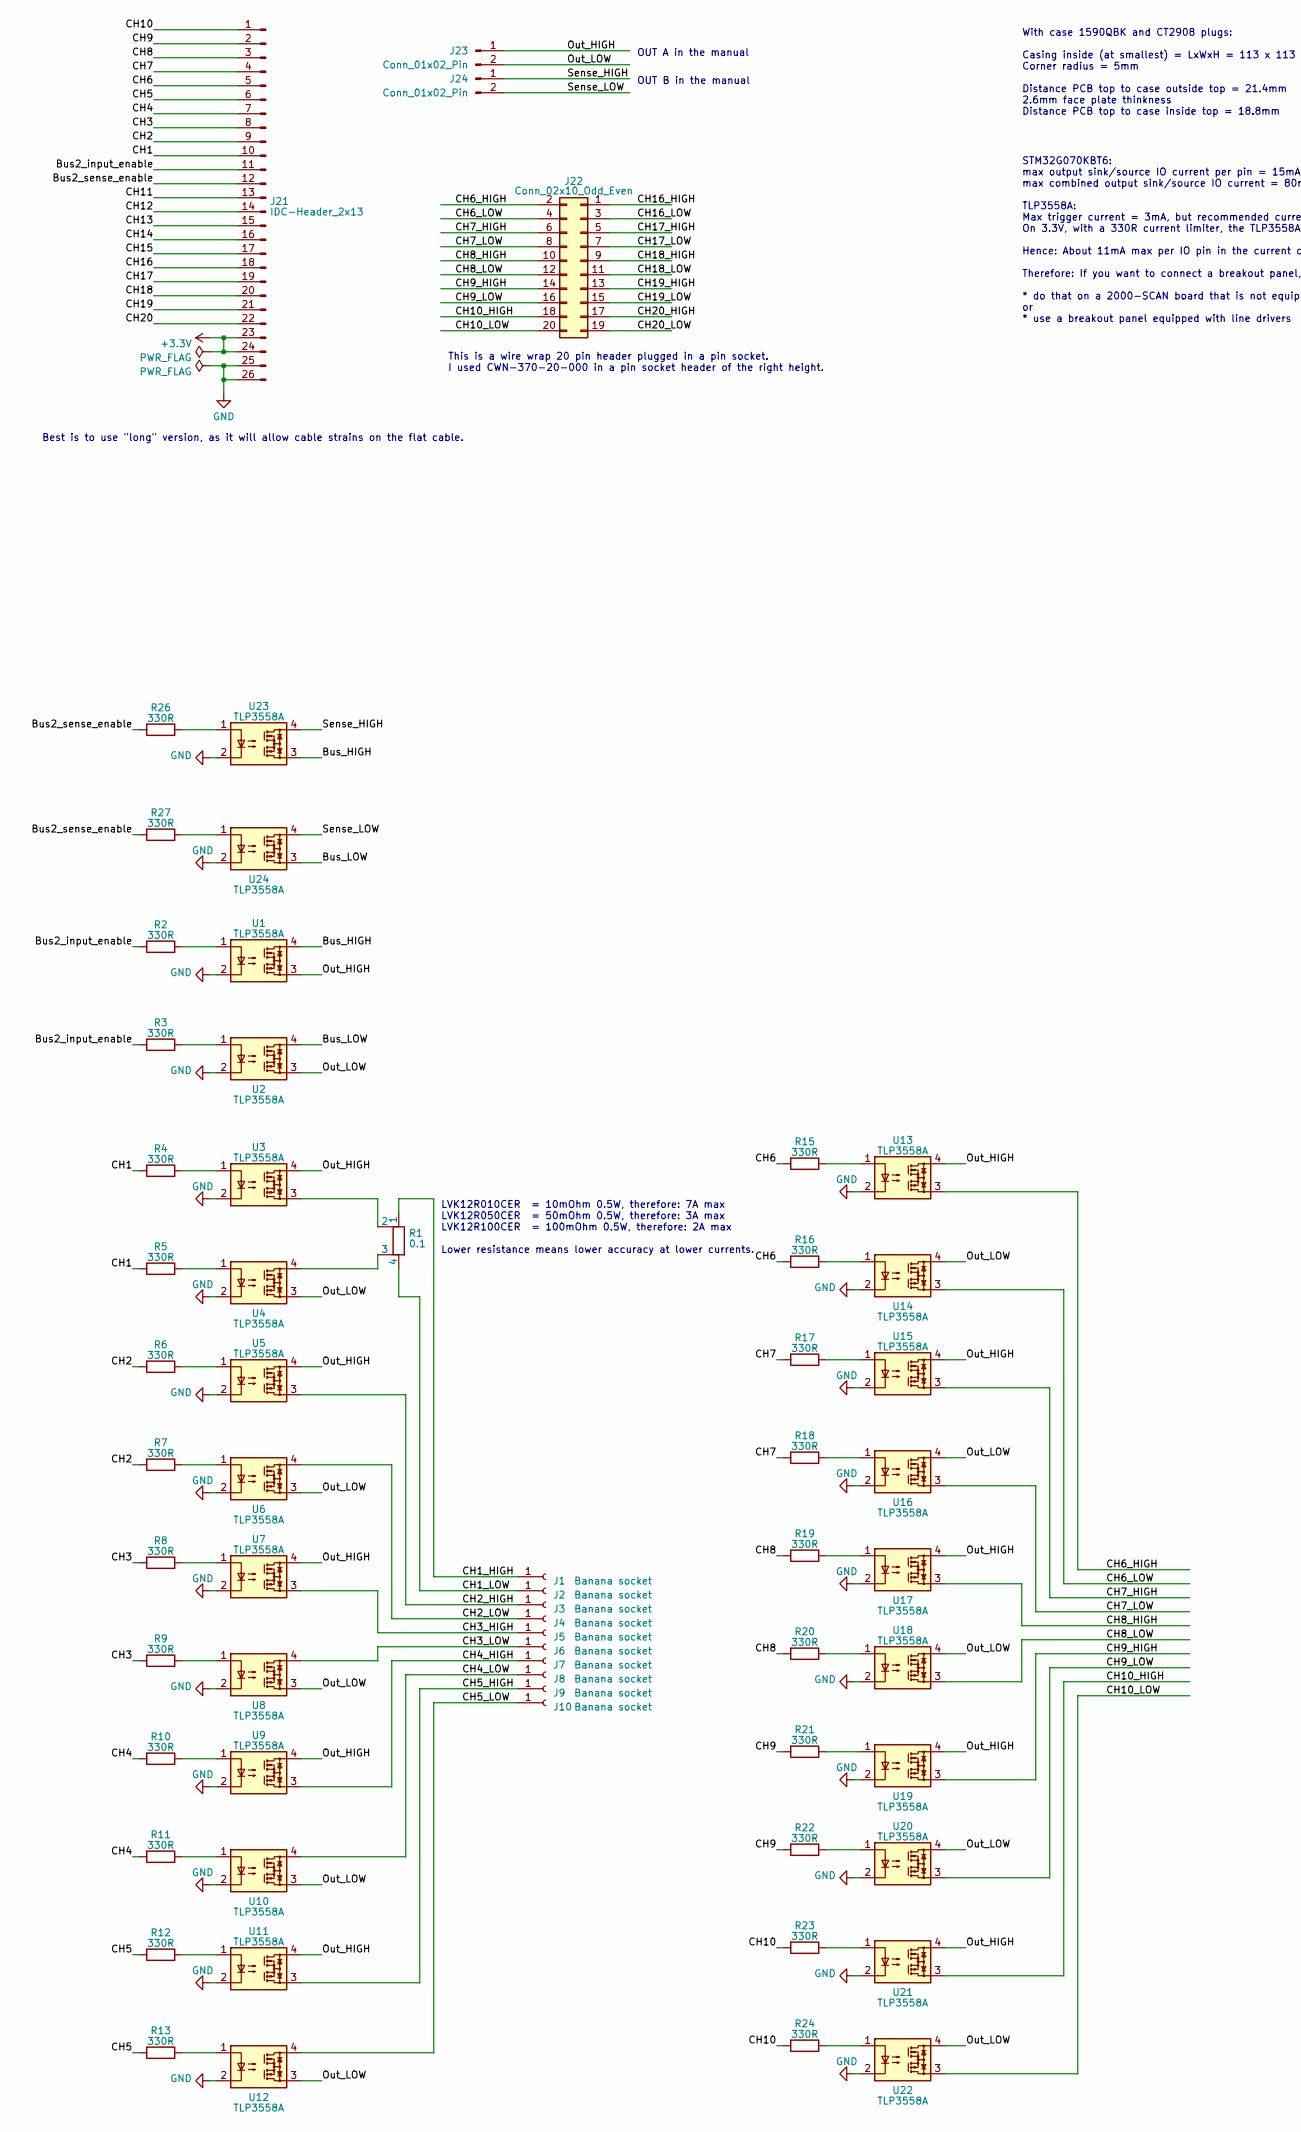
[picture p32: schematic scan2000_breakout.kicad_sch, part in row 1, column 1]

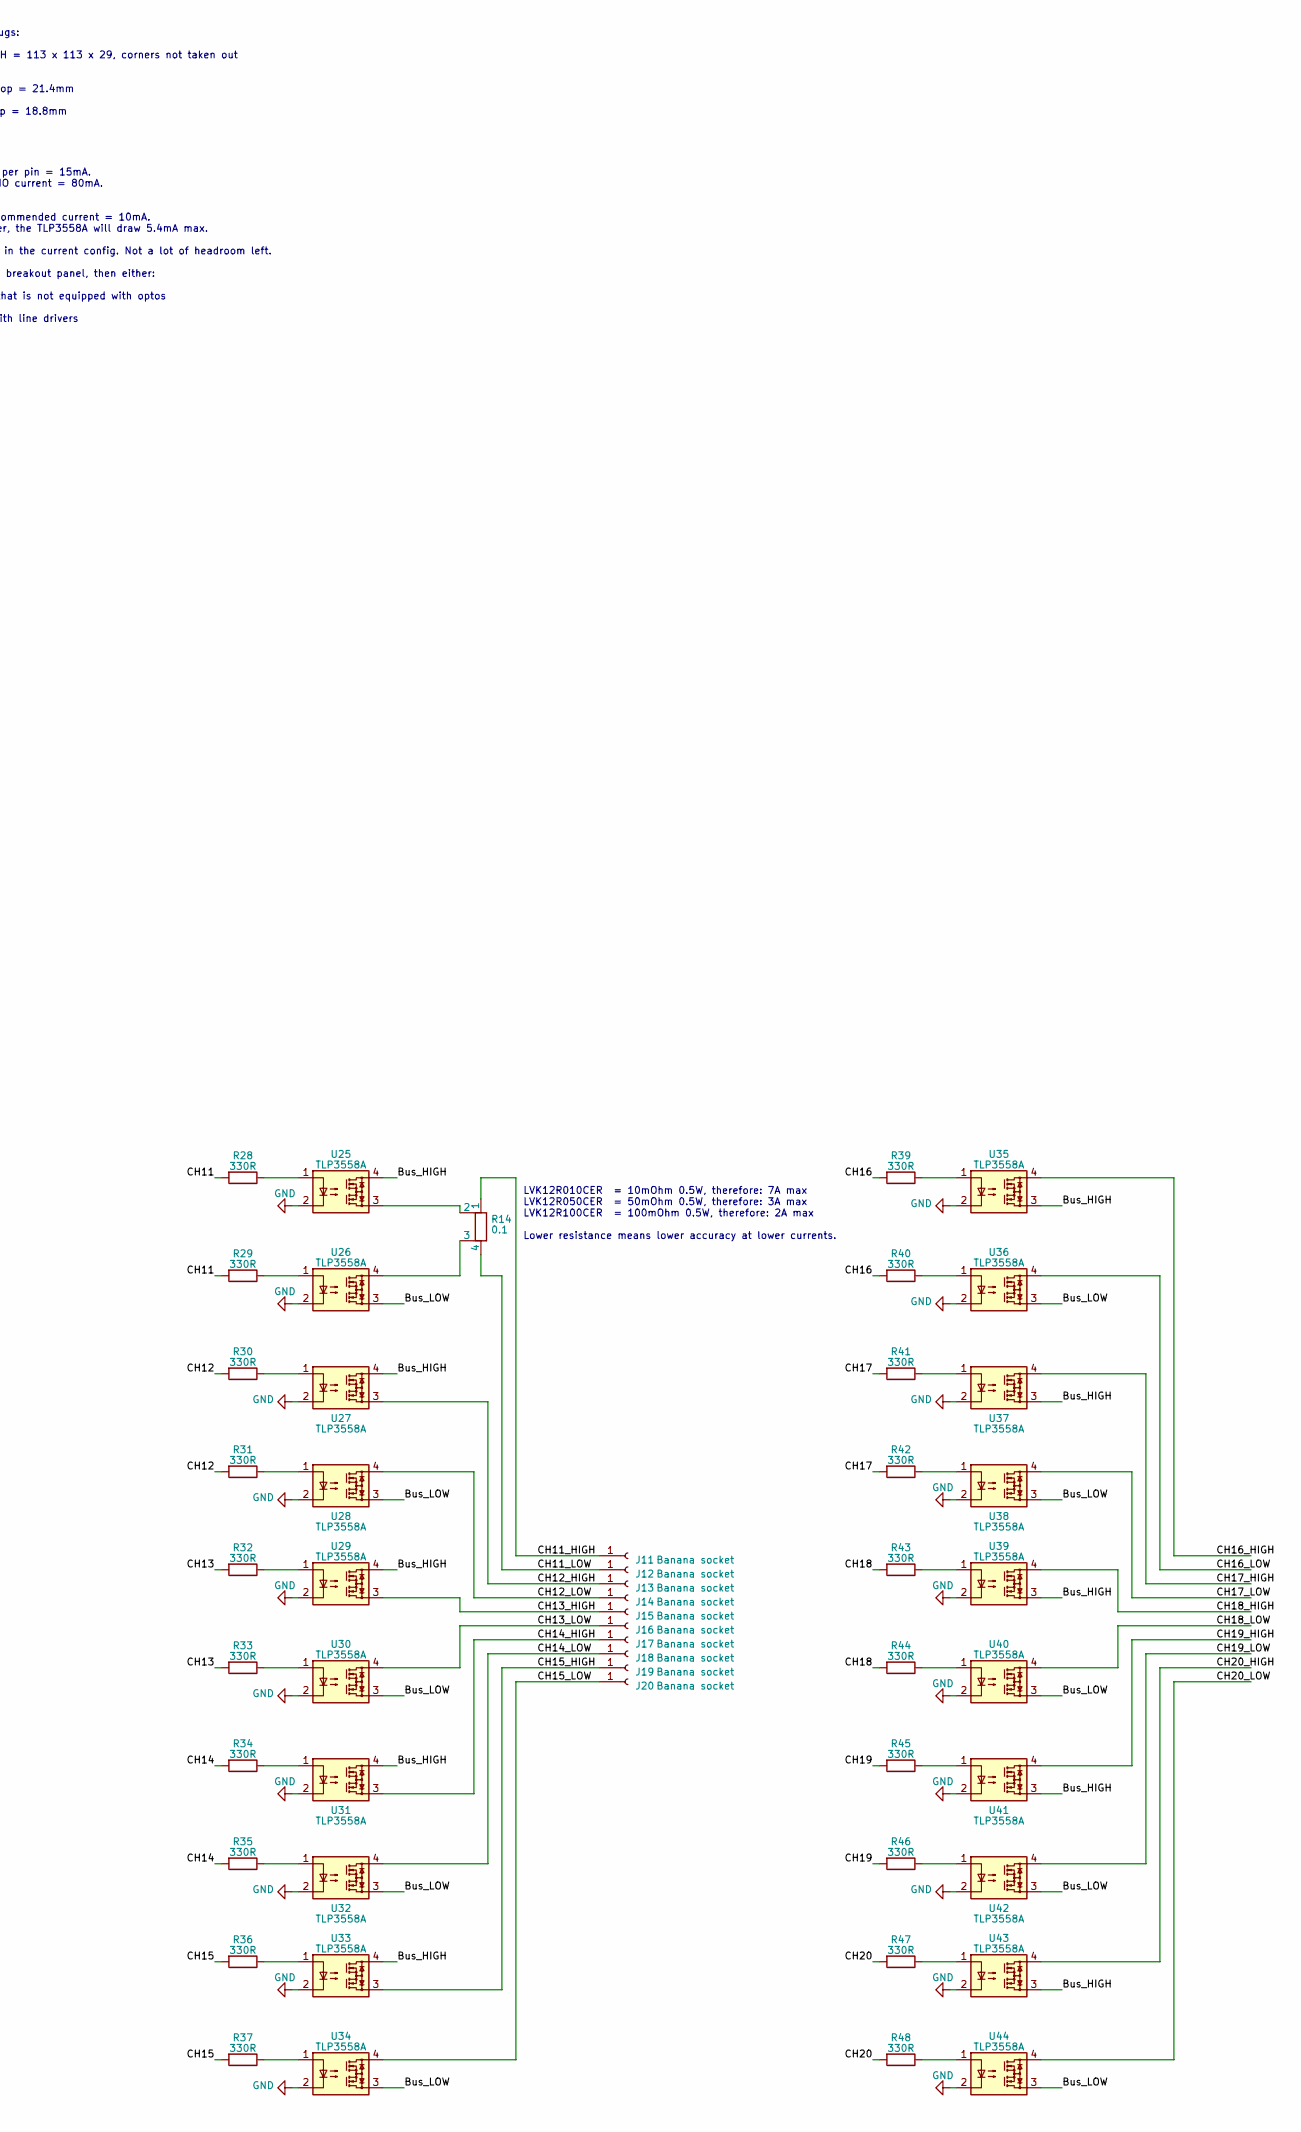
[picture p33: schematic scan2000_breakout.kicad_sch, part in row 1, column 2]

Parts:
J1, J3, J5, J7, J9, J11, J13, J15, J17, J19: Banana socket; CT2908-1
J2, J4, J6, J8, J10, J12, J14, J16, J18, J20: Banana socket; CT2908-0
J21: IDC-Header_2x13; IDC-Header_2x13_P2.54mm_Latch_Horizontal
J22: Conn_02x10_Odd_Even; PinSocket_2x10_P2.54mm_Vertical
J23, J24: Conn_01x02_Pin; PhoenixContact_MSTBA_2,5_2-G-5,08_1x02_P5.08mm_Horizontal
R1, R14: 0.1; R_Shunt_Ohmite_LVK12_ALT2
R2, R3, R4, R5, R6, R7, R8, R9, R10, R11, R12, R13, R15, R16, R17, R18, R19, R20, R21, R22, R23, R24, R26, R27, R28, R29, R30, R31, R32, R33, R34, R35, R36, R37, R39, R40, R41, R42, R43, R44, R45, R46, R47, R48: 330R; R_0603_1608Metric
U1, U2, U3, U4, U5, U6, U7, U8, U9, U10, U11, U12, U13, U14, U15, U16, U17, U18, U19, U20, U21, U22, U23, U24, U25, U26, U27, U28, U29, U30, U31, U32, U33, U34, U35, U36, U37, U38, U39, U40, U41, U42, U43, U44: TLP3558A; DIP-4_W7.62mm

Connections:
+3.3V: J21.23, J21.24
/Bus2_input_enable: J21.11, R2.2, R3.2
/Bus2_sense_enable: J21.12, R26.2, R27.2
/Bus_HIGH: U1.4, U23.3, U25.4, U27.4, U29.4, U31.4, U33.4, U35.3, U37.3, U39.3, U41.3, U43.3
/Bus_LOW: U2.4, U24.3, U26.3, U28.3, U30.3, U32.3, U34.3, U36.3, U38.3, U40.3, U42.3, U44.3
/CH1: J21.10, R4.2, R5.2
/CH1_HIGH: J1.1, R1.1
/CH1_LOW: J2.1, R1.4
/CH2: J21.9, R6.2, R7.2
/CH2_HIGH: J3.1, U5.3
/CH2_LOW: J4.1, U6.4
/CH3: J21.8, R8.2, R9.2
/CH3_HIGH: J5.1, U7.3
/CH3_LOW: J6.1, U8.4
/CH4: J21.7, R10.2, R11.2
/CH4_HIGH: J7.1, U9.3
/CH4_LOW: J8.1, U10.4
/CH5: J21.6, R12.2, R13.2
/CH5_HIGH: J9.1, U11.3
/CH5_LOW: J10.1, U12.4
/CH6: J21.5, R15.2, R16.2
/CH6_HIGH: J22.2, U13.3
/CH6_LOW: J22.4, U14.3
/CH7: J21.4, R17.2, R18.2
/CH7_HIGH: J22.6, U15.3
/CH7_LOW: J22.8, U16.3
/CH8: J21.3, R19.2, R20.2
/CH8_HIGH: J22.10, U17.3
/CH8_LOW: J22.12, U18.3
/CH9: J21.2, R21.2, R22.2
/CH9_HIGH: J22.14, U19.3
/CH9_LOW: J22.16, U20.3
/CH10: J21.1, R23.2, R24.2
/CH10_HIGH: J22.18, U21.3
/CH10_LOW: J22.20, U22.3
/CH11: J21.13, R28.2, R29.2
/CH11_HIGH: J11.1, R14.1
/CH11_LOW: J12.1, R14.4
/CH12: J21.14, R30.2, R31.2
/CH12_HIGH: J13.1, U27.3
/CH12_LOW: J14.1, U28.4
/CH13: J21.15, R32.2, R33.2
/CH13_HIGH: J15.1, U29.3
/CH13_LOW: J16.1, U30.4
/CH14: J21.16, R34.2, R35.2
/CH14_HIGH: J17.1, U31.3
/CH14_LOW: J18.1, U32.4
/CH15: J21.17, R36.2, R37.2
/CH15_HIGH: J19.1, U33.3
/CH15_LOW: J20.1, U34.4
/CH16: J21.18, R39.2, R40.2
/CH16_HIGH: J22.1, U35.4
/CH16_LOW: J22.3, U36.4
/CH17: J21.19, R41.2, R42.2
/CH17_HIGH: J22.5, U37.4
/CH17_LOW: J22.7, U38.4
/CH18: J21.20, R43.2, R44.2
/CH18_HIGH: J22.9, U39.4
/CH18_LOW: J22.11, U40.4
/CH19: J21.21, R45.2, R46.2
/CH19_HIGH: J22.13, U41.4
/CH19_LOW: J22.15, U42.4
/CH20: J21.22, R47.2, R48.2
/CH20_HIGH: J22.17, U43.4
/CH20_LOW: J22.19, U44.4
/Out_HIGH: J23.1, U1.3, U3.4, U5.4, U7.4, U9.4, U11.4, U13.4, U15.4, U17.4, U19.4, U21.4
/Out_LOW: J23.2, U2.3, U4.3, U6.3, U8.3, U10.3, U12.3, U14.4, U16.4, U18.4, U20.4, U22.4
/Sense_HIGH: J24.1, U23.4
/Sense_LOW: J24.2, U24.4
GND: J21.25, J21.26, U1.2, U2.2, U3.2, U4.2, U5.2, U6.2, U7.2, U8.2, U9.2, U10.2, U11.2, U12.2, U13.2, U14.2, U15.2, U16.2, U17.2, U18.2, U19.2, U20.2, U21.2, U22.2, U23.2, U24.2, U25.2, U26.2, U27.2, U28.2, U29.2, U30.2, U31.2, U32.2, U33.2, U34.2, U35.2, U36.2, U37.2, U38.2, U39.2, U40.2, U41.2, U42.2, U43.2, U44.2
unnamed: R1.2, U3.3
unnamed: R1.3, U4.4
unnamed: R2.1, U1.1
unnamed: R3.1, U2.1
unnamed: R4.1, U3.1
unnamed: R5.1, U4.1
unnamed: R6.1, U5.1
unnamed: R7.1, U6.1
unnamed: R8.1, U7.1
unnamed: R9.1, U8.1
unnamed: R10.1, U9.1
unnamed: R11.1, U10.1
unnamed: R12.1, U11.1
unnamed: R13.1, U12.1
unnamed: R14.2, U25.3
unnamed: R14.3, U26.4
unnamed: R15.1, U13.1
unnamed: R16.1, U14.1
unnamed: R17.1, U15.1
unnamed: R18.1, U16.1
unnamed: R19.1, U17.1
unnamed: R20.1, U18.1
unnamed: R21.1, U19.1
unnamed: R22.1, U20.1
unnamed: R23.1, U21.1
unnamed: R24.1, U22.1
unnamed: R26.1, U23.1
unnamed: R27.1, U24.1
unnamed: R28.1, U25.1
unnamed: R29.1, U26.1
unnamed: R30.1, U27.1
unnamed: R31.1, U28.1
unnamed: R32.1, U29.1
unnamed: R33.1, U30.1
unnamed: R34.1, U31.1
unnamed: R35.1, U32.1
unnamed: R36.1, U33.1
unnamed: R37.1, U34.1
unnamed: R39.1, U35.1
unnamed: R40.1, U36.1
unnamed: R41.1, U37.1
unnamed: R42.1, U38.1
unnamed: R43.1, U39.1
unnamed: R44.1, U40.1
unnamed: R45.1, U41.1
unnamed: R46.1, U42.1
unnamed: R47.1, U43.1
unnamed: R48.1, U44.1

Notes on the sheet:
LVK12R010CER = 10mOhm 0.5W, therefore: 7A max LVK12R050CER = 50mOhm 0.5W, therefore: 3A max LVK12R100CER = 100mOhm 0.5W, therefore: 2A max Lower resistance means lower accuracy at lower currents.
Best is to use "long" version, as it will allow cable strains on the flat cable.
OUT B in the manual
STM32G070KBT6: max output sink/source IO current per pin = 15mA. max combined output sink/source IO current = 80mA. TLP3558A: Max trigger current = 3mA, but recommended current = 10mA. On 3.3V, with a 330R current limiter, the TLP3558A will draw 5.4mA max. Hence: About 11mA max per IO pin in the cu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
OUT A in the manual
With case 1590QBK and CT2908 plugs: Casing inside (at smallest) = LxWxH = 113 x 113 x 29, corners not taken out Corner radius = 5mm Distance PCB top to case outside top = 21.4mm 2.6mm face plate thinkness Distance PCB top to case inside top = 18.8mm
This is a wire wrap 20 pin header plugged in a pin socket. I used CWN-370-20-000 in a pin socket header of the right height.

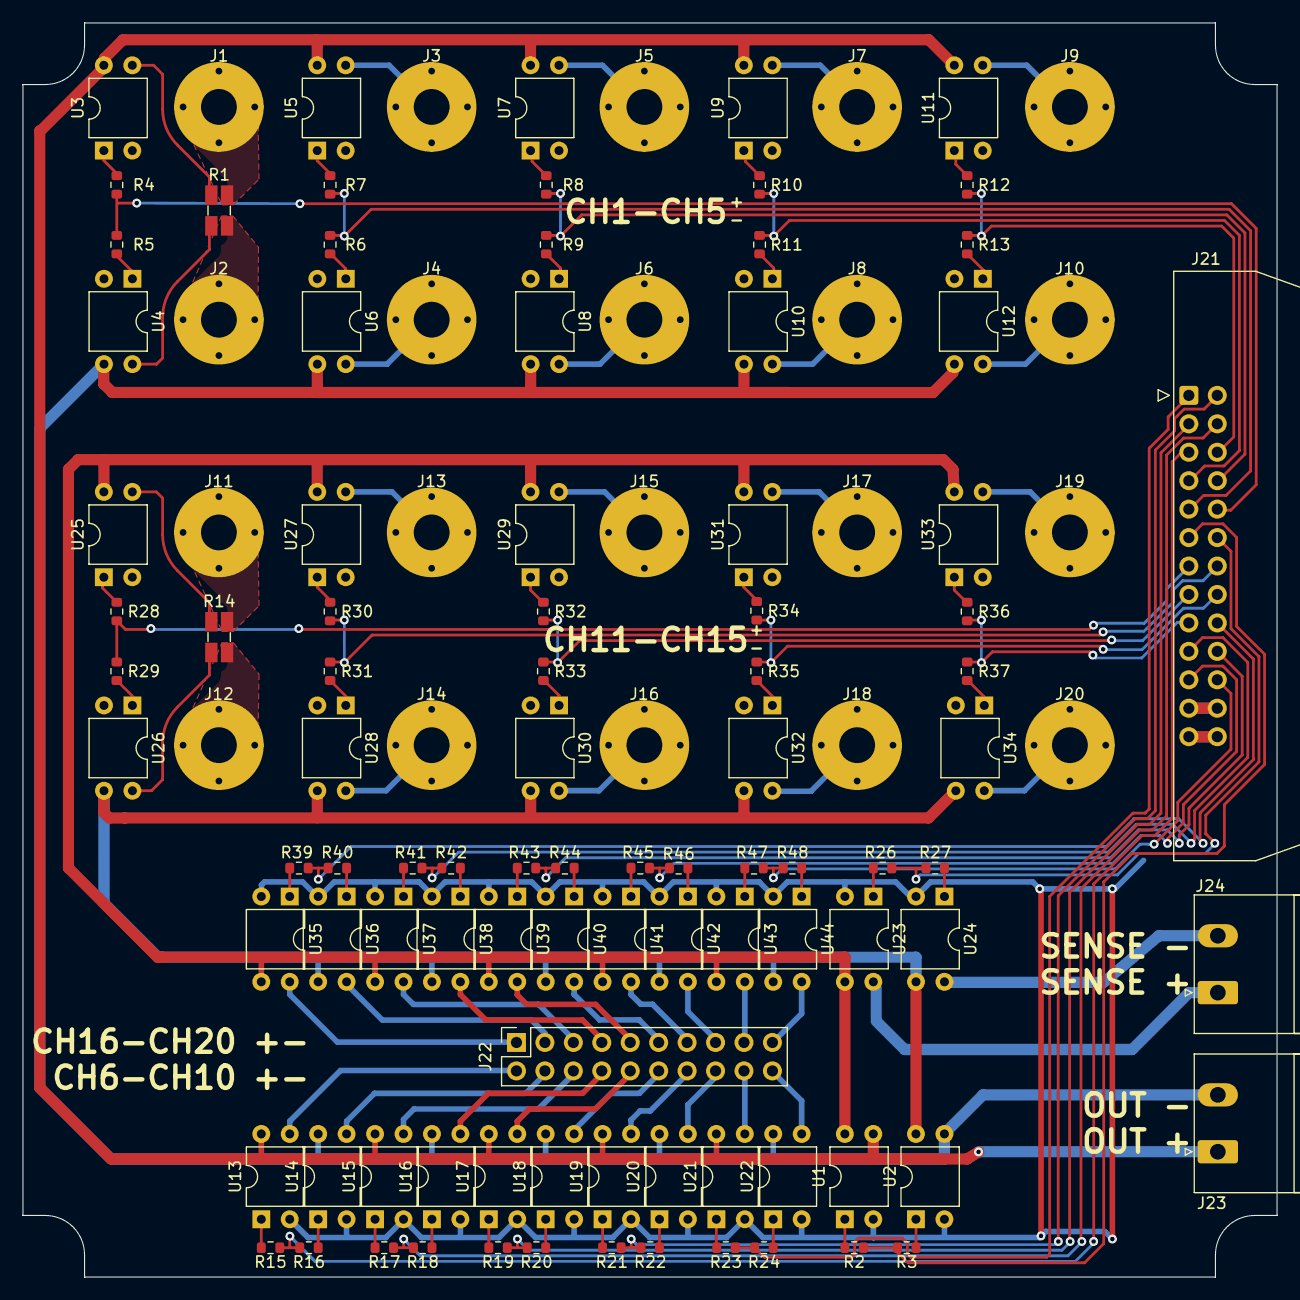
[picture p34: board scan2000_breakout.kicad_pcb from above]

Board: 2 copper layers, 112.0 x 112.0 mm, 114 parts (0 on the bottom side), 118 nets.

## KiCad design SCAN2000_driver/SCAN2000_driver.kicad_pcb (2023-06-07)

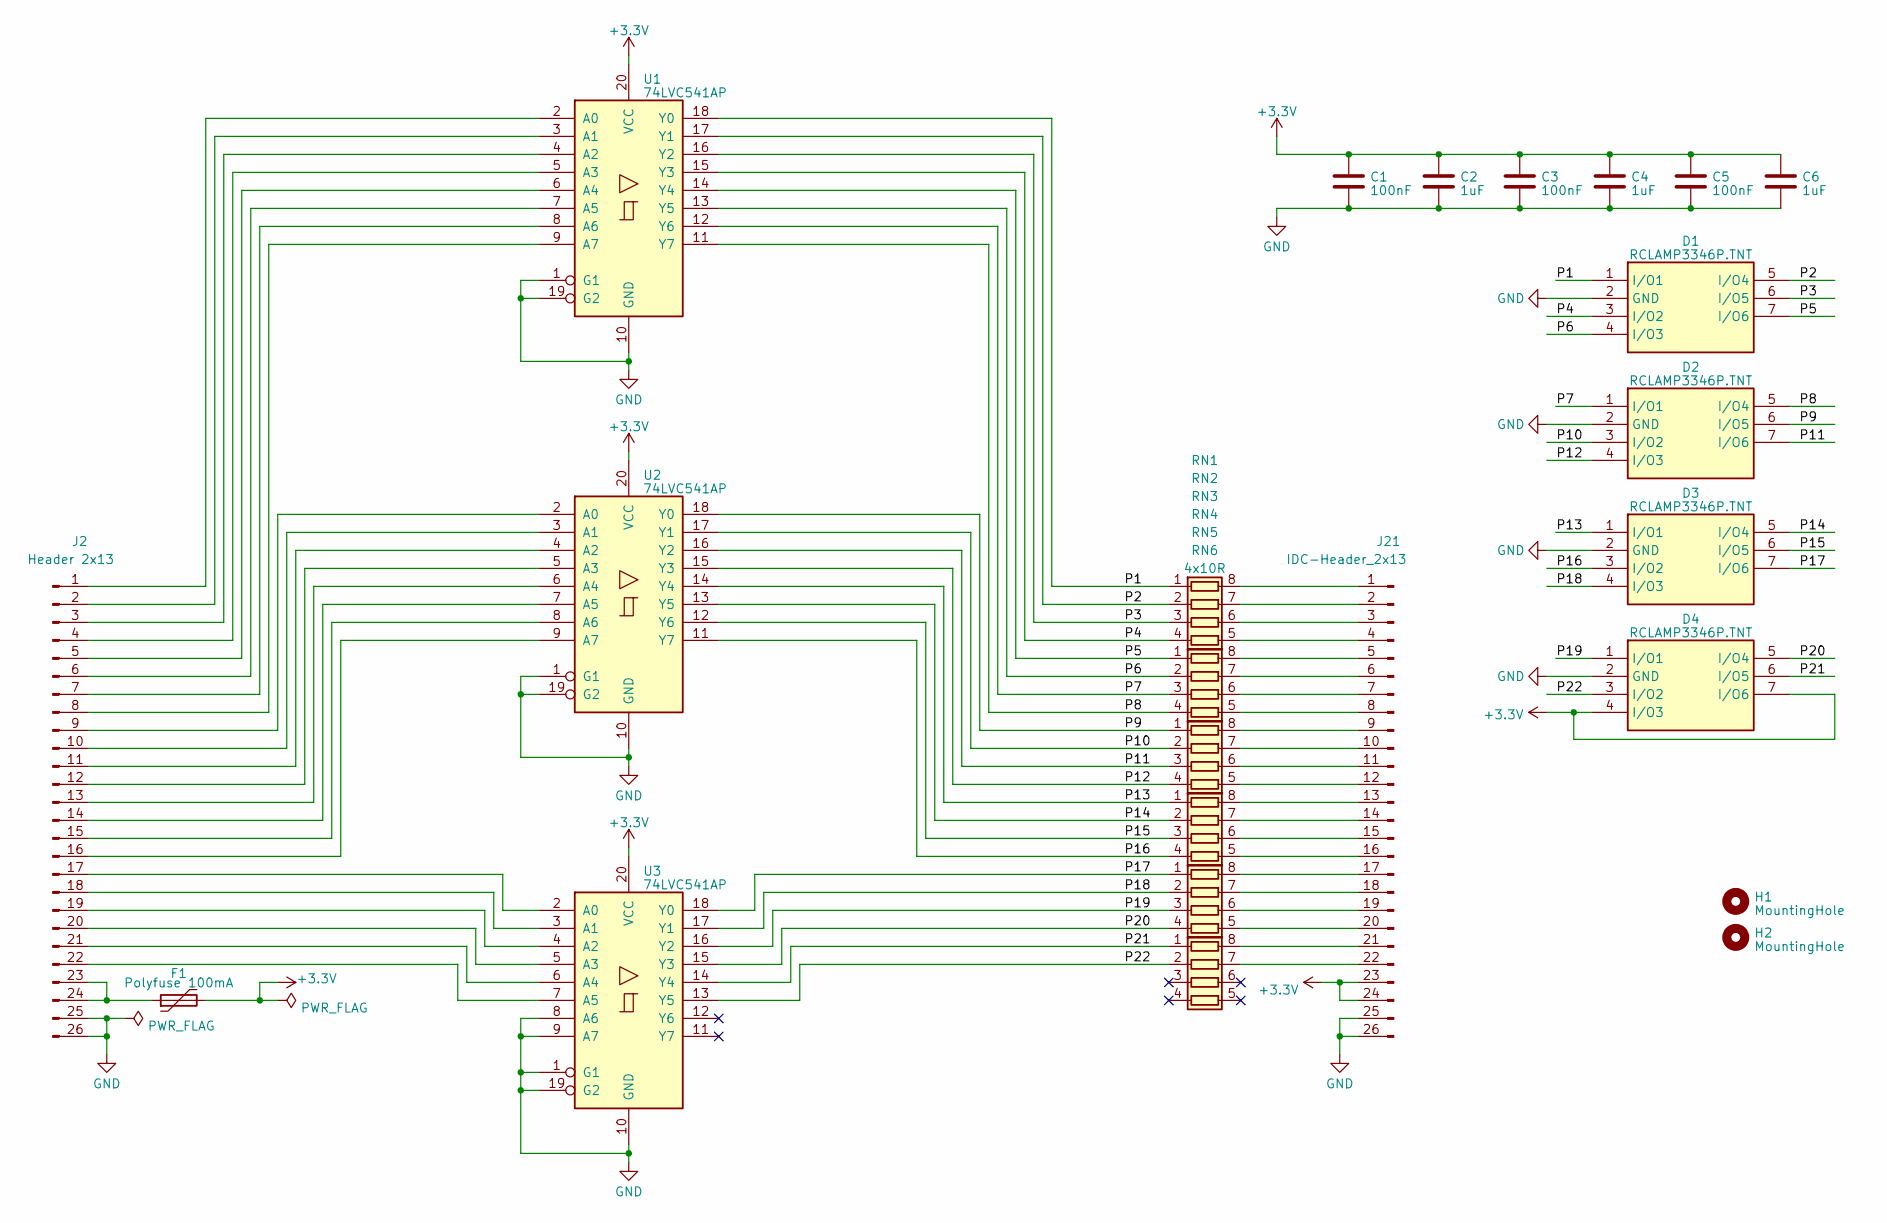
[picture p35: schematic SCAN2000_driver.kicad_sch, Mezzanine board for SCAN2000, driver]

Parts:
C1, C3, C5: 100nF; C_0603_1608Metric_Pad1.08x0.95mm_HandSolder
C2, C4, C6: 1uF; C_0805_2012Metric_Pad1.18x1.45mm_HandSolder
D1, D2, D3, D4: RCLAMP3346P.TNT; RCLAMP3346PQTNT; Manufacturer_Part_Number RCLAMP3346P.TNT; Mouser Part Number 947-RCLAMP3346P.TNT
F1: Polyfuse 100mA; R_1206_3216Metric_Pad1.30x1.75mm_HandSolder
H1, H2: MountingHole; MountingHole_3.2mm_M3_DIN965
J2: Header 2x13; PinHeader_2x13_P2.54mm_Vertical
J21: IDC-Header_2x13; IDC-Header_2x13_P2.54mm_Latch_Horizontal
RN1, RN2, RN3, RN4, RN5, RN6: 4x10R; R_Array_Convex_4x0603
U1, U2, U3: 74LVC541AP; TSSOP-20_4.4x6.5mm_P0.65mm

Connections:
+3.3V: C1.1, C2.1, C3.1, C4.1, C5.1, C6.1, D4.4 (I/O3), D4.7 (I/O6), F1.2, U1.20 (VCC), U2.20 (VCC), U3.20 (VCC); also elsewhere on the board
/P1: D1.1 (I/O1), RN1.1 (R1.1), U1.18 (Y0)
/P2: D1.5 (I/O4), RN1.2 (R2.1), U1.17 (Y1)
/P3: D1.6 (I/O5), RN1.3 (R3.1), U1.16 (Y2)
/P4: D1.3 (I/O2), RN1.4 (R4.1), U1.15 (Y3)
/P5: D1.7 (I/O6), RN2.1 (R1.1), U1.14 (Y4)
/P6: D1.4 (I/O3), RN2.2 (R2.1), U1.13 (Y5)
/P7: D2.1 (I/O1), RN2.3 (R3.1), U1.12 (Y6)
/P8: D2.5 (I/O4), RN2.4 (R4.1), U1.11 (Y7)
/P9: D2.6 (I/O5), RN3.1 (R1.1), U2.18 (Y0)
/P10: D2.3 (I/O2), RN3.2 (R2.1), U2.17 (Y1)
/P11: D2.7 (I/O6), RN3.3 (R3.1), U2.16 (Y2)
/P12: D2.4 (I/O3), RN3.4 (R4.1), U2.15 (Y3)
/P13: D3.1 (I/O1), RN4.1 (R1.1), U2.14 (Y4)
/P14: D3.5 (I/O4), RN4.2 (R2.1), U2.13 (Y5)
/P15: D3.6 (I/O5), RN4.3 (R3.1), U2.12 (Y6)
/P16: D3.3 (I/O2), RN4.4 (R4.1), U2.11 (Y7)
/P17: D3.7 (I/O6), RN5.1 (R1.1), U3.18 (Y0)
/P18: D3.4 (I/O3), RN5.2 (R2.1), U3.17 (Y1)
/P19: D4.1 (I/O1), RN5.3 (R3.1), U3.16 (Y2)
/P20: D4.5 (I/O4), RN5.4 (R4.1), U3.15 (Y3)
/P21: D4.6 (I/O5), RN6.1 (R1.1), U3.14 (Y4)
/P22: D4.3 (I/O2), RN6.2 (R2.1), U3.13 (Y5)
GND: C1.2, C2.2, C3.2, C4.2, C5.2, C6.2, D1.2 (GND), D2.2 (GND), D3.2 (GND), D4.2 (GND), J2.25, J2.26, U1.1 (G1), U1.10 (GND), U1.19 (G2), U2.1 (G1), U2.10 (GND), U2.19 (G2), U3.1 (G1), U3.8 (A6), U3.9 (A7), U3.10 (GND), U3.19 (G2); also elsewhere on the board
unnamed 24: RN1.8 (R1.2); also elsewhere on the board
unnamed 25: RN1.7 (R2.2); also elsewhere on the board
unnamed 26: RN1.6 (R3.2); also elsewhere on the board
unnamed 27: RN1.5 (R4.2); also elsewhere on the board
unnamed 28: RN2.8 (R1.2); also elsewhere on the board
unnamed 29: RN2.7 (R2.2); also elsewhere on the board
unnamed 30: RN2.6 (R3.2); also elsewhere on the board
unnamed 31: RN2.5 (R4.2); also elsewhere on the board
unnamed 32: RN3.8 (R1.2); also elsewhere on the board
unnamed 33: RN3.7 (R2.2); also elsewhere on the board
unnamed 34: RN3.6 (R3.2); also elsewhere on the board
unnamed 35: RN3.5 (R4.2); also elsewhere on the board
unnamed 36: RN4.8 (R1.2); also elsewhere on the board
unnamed 37: RN4.7 (R2.2); also elsewhere on the board
unnamed 38: RN4.6 (R3.2); also elsewhere on the board
unnamed 39: RN4.5 (R4.2); also elsewhere on the board
unnamed 40: RN5.8 (R1.2); also elsewhere on the board
unnamed 41: RN5.7 (R2.2); also elsewhere on the board
unnamed 42: RN5.6 (R3.2); also elsewhere on the board
unnamed 43: RN5.5 (R4.2); also elsewhere on the board
unnamed 44: RN6.8 (R1.2); also elsewhere on the board
unnamed 45: RN6.7 (R2.2); also elsewhere on the board
unnamed: J2.1, U1.2 (A0)
unnamed: J2.2, U1.3 (A1)
unnamed: J2.3, U1.4 (A2)
unnamed: J2.4, U1.5 (A3)
unnamed: J2.5, U1.6 (A4)
unnamed: J2.6, U1.7 (A5)
unnamed: J2.7, U1.8 (A6)
unnamed: J2.8, U1.9 (A7)
unnamed: J2.9, U2.2 (A0)
unnamed: J2.10, U2.3 (A1)
unnamed: J2.11, U2.4 (A2)
unnamed: J2.12, U2.5 (A3)
unnamed: J2.13, U2.6 (A4)
unnamed: J2.14, U2.7 (A5)
unnamed: J2.15, U2.8 (A6)
unnamed: J2.16, U2.9 (A7)
unnamed: J2.17, U3.2 (A0)
unnamed: J2.18, U3.3 (A1)
unnamed: J2.19, U3.4 (A2)
unnamed: J2.20, U3.5 (A3)
unnamed: J2.21, U3.6 (A4)
unnamed: J2.22, U3.7 (A5)
unnamed: F1.1, J2.23, J2.24

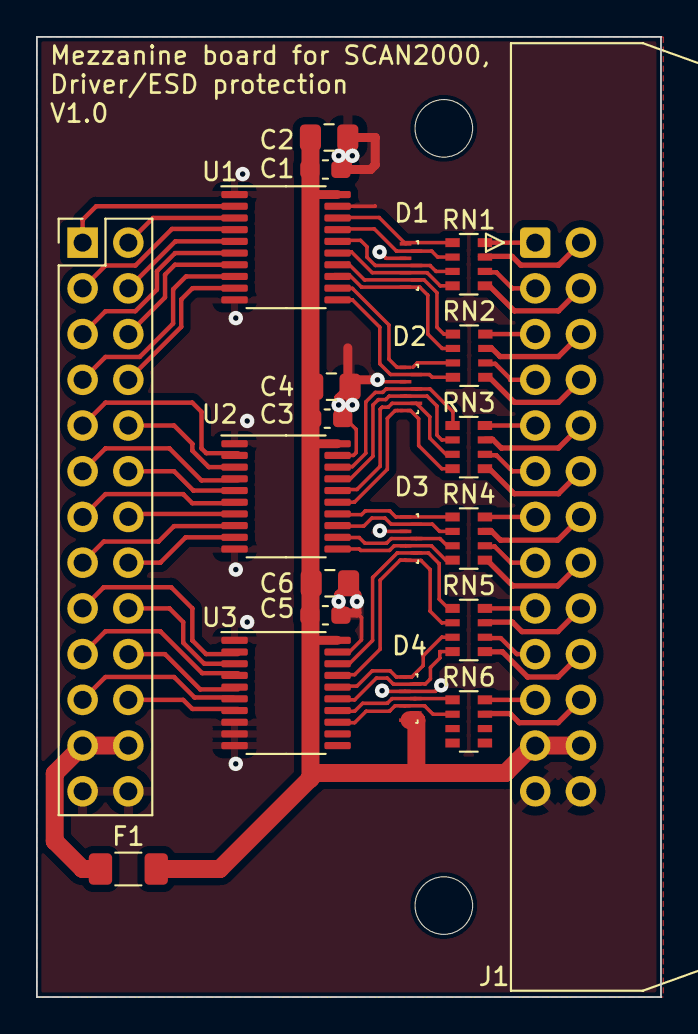
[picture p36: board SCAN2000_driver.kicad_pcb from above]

Board: 2 copper layers, 34.7 x 53.3 mm, 24 parts (0 on the bottom side), 69 nets.

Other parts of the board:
J1: IDC-Header_2x13; IDC-Header_2x13_P2.54mm_Latch_Horizontal

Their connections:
+3.3V: J1.23, J1.24; also elsewhere on the board
GND: J1.25, J1.26; also elsewhere on the board
unnamed 24: J1.1; also elsewhere on the board
unnamed 25: J1.2; also elsewhere on the board
unnamed 26: J1.3; also elsewhere on the board
unnamed 27: J1.4; also elsewhere on the board
unnamed 28: J1.5; also elsewhere on the board
unnamed 29: J1.6; also elsewhere on the board
unnamed 30: J1.7; also elsewhere on the board
unnamed 31: J1.8; also elsewhere on the board
unnamed 32: J1.9; also elsewhere on the board
unnamed 33: J1.10; also elsewhere on the board
unnamed 34: J1.11; also elsewhere on the board
unnamed 35: J1.12; also elsewhere on the board
unnamed 36: J1.13; also elsewhere on the board
unnamed 37: J1.14; also elsewhere on the board
unnamed 38: J1.15; also elsewhere on the board
unnamed 39: J1.16; also elsewhere on the board
unnamed 40: J1.17; also elsewhere on the board
unnamed 41: J1.18; also elsewhere on the board
unnamed 42: J1.19; also elsewhere on the board
unnamed 43: J1.20; also elsewhere on the board
unnamed 44: J1.21; also elsewhere on the board
unnamed 45: J1.22; also elsewhere on the board

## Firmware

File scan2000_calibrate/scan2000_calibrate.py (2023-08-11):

# SCAN2000 shunt linearity measurement
# via SCPI
# Current source: 4 Quadrant enabled HP 66332A (option 760, relay board)
# Current measurement/Calibrator: K34465A. Must have done a fresh ACAL before!
# Target: DMM6500 with SCAN2000-20, with shunts on channels 1 and 11

# How to use: connect the current source on the series connection of the current 
# measurement device + CH1 + CH11.
# This script walks through a range of current values, and measures the "real" current 
# and compares that to the voltage reading in the channels 1 and 11
# As the current source is somewhat noisy, it measures the current and the voltage simultaneously, and for the same duration.
# Since I cannot read channel 1 and 11 at the same time, I must do 2 measurement sets per current level set:
# one for channel 1, and one for channel 11.
#
# The result is a CSV file with (current in A, Voltage in V):
# "nr": line/test sequence number
# "set" the set current
# "actual1": current read while measuring channel 1 
# "actual11": current read while measuring channel 11 
# "ch1": voltage on channel 1
# "ch11": voltage on channel 11
# "avg_actual": average current read
# "abs_actual": average current read, absolute value
# "m_ch1": multiplication factor CH1: actual1/ch1
# "m_ch11": multiplication factor CH11: actual11/ch11
# "ch_range" range while reading voltage on ch1 and ch11. In case of a difference between the 2 measurements: average of the 2.
# "curr_range": range while reading current. In case of a difference between the 2 measurements: average of the 2.
#
# TODO: This script is robust against the/my? DMM6500's tendency to sometimes lose a command.

# TODO: sync the current measurements. Right now the results are noisy in low amps because the current source is noisy.
# TODO: do measurements with a 4 Quadrant enabled HP 6634B, as that has better low current behaviour

import pyvisa as visa
import serial
import time
import csv

# the global vars of the devices
ser = serial.Serial()
dev_cm = None
dev_target = None

DEBUG = False

# SCPI Addresses:
# Current source: USB, prologix USB-GPIB, address 1. Hence: not via pyvisa, as that is not stable for that adapter.
ADDR_SOURCE = "/dev/cu.usbmodem31401"
ADDR_SOURCE_SUBADDR = "1"
AUTOREAD = False
SERIAL_TIMEOUT = 0.1
# Calibrator:
ADDR_CALIBRATOR = "TCPIP::192.168.7.201::INSTR"
NPLC_MAX_CALIBRATOR = 100
# MEASUREMENT_TYPE_CALIBRATOR = "VOLT:DC"
MEASUREMENT_TYPE_CALIBRATOR = "CURR:DC"
# do autorange on calibrator. That clicks a lot.
AUTORANGE_CAL = False

# Target
ADDR_TARGET = "TCPIP::192.168.7.205::INSTR"
NPLC_MAX_TARGET = 10

# Switching off auto zero improves timing alignment of the measurements A LOT. It however introduces long term drift.
# So when using a noisy current source, do not do AZERO
AZERO = False
# Display OFF slightly improves speed
DISPLAY_OFF = False

OUTFILE = "out.csv"

# my shunts go to 2A
CURRENT_MAX = 2
# go 5% steps up. Easy way to get a close to logarithmic test.
CURRENT_STEPS_PERC = 5
# the HP 66332A only has 2mA programming accuracy with about 0.5mA error margin.
CURRENT_RESOLUTION = 0.001

# Set the aperture (expressed in PLC). Must be 1..NPLC_MAX_CALIBRATOR
MEASUREMENT_NPLC = 10


def sendSerialCmdRaw(cmd):
    bcmd = bytearray()
    bcmd.extend(cmd.encode("ascii"))
    bcmd.append(0x0D)  # CR
    bcmd.append(0x0A)  # LF
    ser.write(bcmd)


def sendSerialCmd(cmd, readReply=True, delaysecs=0):
    global ser
    if DEBUG:
        if not readReply:
            print(f"Sending: {cmd}")
        else:
            print(f"Sending: {cmd} : ", end="")
    sendSerialCmdRaw(cmd)
    if readReply:
        if delaysecs > 0:
            time.sleep(delaysecs)
        if not AUTOREAD:
            sendSerialCmdRaw("++read eoi")
        s = ser.read(256)
        retstr = s.decode("ascii")
        if DEBUG:
            print(f"{retstr} ({len(s)}b)")
        return retstr
    else:
        s = ser.read(256)
        return None


def inst_cs_query(cmd):
    return sendSerialCmd(cmd, True)


def inst_cs_write(cmd):
    return sendSerialCmd(cmd, False)


def inst_cs_init():
    global ser

    port = ADDR_SOURCE
    addr = ADDR_SOURCE_SUBADDR
    baudrate = 38400  # 115200

    ser = serial.Serial(port, baudrate=baudrate, timeout=SERIAL_TIMEOUT)

    sendSerialCmd("++mode 1", False)  # controller mode (the only mode it supports)
    if AUTOREAD:
        sendSerialCmd("++auto 1", False)  # no need for "++read eoi"
    else:
        sendSerialCmd("++auto 0", False)  # need for "++read eoi"
    sendSerialCmd("++eos 0", False)  # CR/LF is oes
    sendSerialCmd("++addr " + addr, False)
    sendSerialCmd("++read", False)

    inst_cs_write("*CLS")
    # check ID
    s = inst_cs_query("*IDN?").strip()
    if "66332A" not in s:
        print(f'ERROR: device ID is unexpected: "{s}"')
        return False

    # output off, voltage 2V, current 0
    inst_cs_write("OUTP 0")
    inst_cs_write("OUTP:REL:POL NORM")
    inst_cs_write("SOUR:VOLT 10")
    inst_cs_write("SOUR:CURR 0")
    s = inst_cs_query("SYST:ERR?").strip()
    if not s.startswith("+0"):
        print(f'ERROR during init: "{s}"')
        return False

    return True


def inst_cs_close():
    inst_cs_write("OUTP 0")
    inst_cs_write("OUTP:REL:POL NORM")
    inst_cs_write("SOUR:VOLT 0")
    inst_cs_write("SOUR:CURR 0")


def inst_cal_init(rm):
    """Init the device

    Args:
        rm (ResourceManager): the global resource manager

    Returns:
        Boolean: success
    """
    global inst_cal
    inst_cal = rm.open_resource(ADDR_CALIBRATOR)

    if MEASUREMENT_NPLC > 10:
        # in ms
        inst_cal.timeout = 10000

    inst_cal.write("*CLS")
    # check ID
    s = inst_cal.query("*IDN?").strip()
    if "34465A" not in s:
        print(f'ERROR: device ID is unexpected: "{s}"')
        return False

    # set to overall config
    inst_cal.write(f"CONF:{MEASUREMENT_TYPE_CALIBRATOR} AUTO")

    # improve for fast use:
    if DISPLAY_OFF:
        inst_cal.write("DISP OFF")

    s = inst_cal.query("SYST:ERR?").strip()
    if not s.startswith("+0"):
        print(f'ERROR during init: "{s}"')
        return False
    return True


def prepareMeasurement_inst_cal(range=None):
    """Prepare the measurement

    Args:
        range (String, optional): range to be set. When None: set to auto range. Defaults to None.

    Returns:
        String: the command to be sent to start the measurement
    """
    global inst_cal
    
    nplc = min(MEASUREMENT_NPLC, NPLC_MAX_CALIBRATOR)

    if range is None:
        nplc = 1
        range = "AUTO"
        
    inst_cal.write(f"CONF:{MEASUREMENT_TYPE_CALIBRATOR} {range}")  # This messes up all of the below. So set it
    if "CURR" in MEASUREMENT_TYPE_CALIBRATOR:
        inst_cal.write("SENS:CURR:DC:TERM 3")
    inst_cal.write(f"SENS:{MEASUREMENT_TYPE_CALIBRATOR}:NPLC {nplc}")
    if AZERO:
        s = "ON"
    else:
        s = "OFF"
    inst_cal.write(f"SENS:{MEASUREMENT_TYPE_CALIBRATOR}:ZERO:AUTO {s}")

    s = inst_cal.query("SYST:ERR?").strip()
    if not s.startswith("+0"):
        print(f'ERROR during prepareMeasurement: "{s}"')
        return None
                    
    # trigger options:
    # 1) TRIG:SOUR IMM ; INIT
    # 2) TRIG:SOUR BUS ; INIT ; *TRG
    inst_cal.write("TRIG:SOUR BUS")
    inst_cal.write("INIT")
    return "*TRG"
    

def getMeasurement_inst_cal():
    """Get the measurement values
    
    Returns:
        float,str: value read, range used
    """
    global inst_cal
    
    inst_cal.write("*WAI")
    s = inst_cal.query("FETCH?").strip()
    f = float(s)
    s = inst_cal.query(f"{MEASUREMENT_TYPE_CALIBRATOR}:RANG?")
    r = str(float(s))  # make it a simplified version. I tend to get stuff back like "+1.00000000E-01". Make it "0.1"
    return f, r


def inst_cal_close():
    inst_cal.write("DISP ON")
    inst_cal.write("SYST:LOCal")


def inst_target_init(rm, channels=None):
    """Init the device

    Args:
        rm (ResourceManager): the global resource manager
        channels (string, optional): list of channels to use. None = front panel only. Defaults to None.

    Returns:
        Boolean: success
    """

    global inst_target
    inst_target = rm.open_resource(ADDR_TARGET)
    
    sChannels = ""
    if channels is not None and len(channels) > 0:
        sChannels = ", (@" + channels + ")"
        
    if MEASUREMENT_NPLC > 10:
        # in ms
        inst_target.timeout = 10000

    inst_target.write("*CLS")

    # check ID
    s = inst_target.query("*IDN?").strip()
    if "DMM6500" not in s:
        print(f'ERROR: device ID is unexpected: "{s}"')
        return False

    # set to voltage measurement
    inst_target.write("SENS:FUNC 'VOLT'" + sChannels)
    inst_target.write("VOLT:DC:RANG:AUTO 1" + sChannels)
    inst_target.write("VOLT:DC:INP AUTO" + sChannels)
    inst_target.write("VOLT:DC:LINE:SYNC 0" + sChannels)
    if AZERO:
        s = "1"
    else:
        s = "0"
    inst_target.write(f"VOLT:DC:AZER {s}" + sChannels)
    
    # improve for fast use:
    if DISPLAY_OFF:
        inst_target.write("DISP:SCR PROC")
    
    s = inst_target.query("SYST:ERR?").strip()
    if not s.startswith("0,\"No error"):
        print(f'ERROR during init: "{s}"')
        return False
    return True


def prepareMeasurement_inst_target(ch=0, range=None):
    """Prepare the measurement

    Args:
        ch (int, optional): Channel to be used. 0 = front panel. Defaults to 0.
        range (String, optional): range to be set. When None: set to auto range. Defaults to None.

    Returns:
        String: the command to be sent to start the measurement
    """
    global inst_target
    # TODO: in rare cases, wildly off measurements get through. Check that.
    
    sChannel = ""
    if ch != 0:
        sChannel = f", (@{ch})"
            
    inst_target.write("ABOR")
    if ch != 0:
        inst_target.write("ROUT:OPEN:ALL")
        inst_target.write(f"ROUT:CLOS (@{ch})")  # without a comma, so directly
        
    nplc = MEASUREMENT_NPLC
    
    if range is None:
        nplc = 1
        inst_target.write("VOLT:DC:RANG:AUTO 1" + sChannel)
    else:
        inst_target.write("VOLT:DC:RANG " + range + sChannel)
        
    avg_filter = 1
    if nplc > NPLC_MAX_TARGET:
        nplc = NPLC_MAX_TARGET
        avg_filter = MEASUREMENT_NPLC / NPLC_MAX_TARGET
    
    inst_target.write(f"SENS:VOLT:NPLC {nplc}" + sChannel)
    
    if avg_filter <= 1:
        inst_target.write("VOLT:DC:AVER 0" + sChannel)
    else:
        inst_target.write(f"VOLT:DC:AVER:COUNT {avg_filter}" + sChannel)
        inst_target.write("VOLT:DC:AVER:TCON REP" + sChannel)
        inst_target.write("VOLT:DC:AVER:STAT 1" + sChannel)

    s = inst_target.query("SYST:ERR?").strip()
    if not s.startswith("0,\"No error"):
        print(f'ERROR during prepareMeasurement: "{s}"')
        return None

    # trigger options:
    # 1) TRIG:LOAD "SimpleLoop", 1 ; INIT
    # .. haven't found a way to use *TRG
    
    # set for immediate trigger
    inst_target.write("TRIG:LOAD \"SimpleLoop\", 1")    
    return "INIT"
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

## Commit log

2023-06-04 First content commit
    [1457L1201EBK.stp, 1457L1601EBK.stp, 1590BB2BK.stp, 1590BBBK.stp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]
2023-06-06 added mezzanine board
    [61202021621_Download_STP_61202021621_rev1.stp, 61202021621_rev1.stp, 61202022821_Download_STP_61202022821_rev1.stp, 61202622121.stp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]
2023-06-07 better doc
    [61202622121.stp, SCAN2000_driver-B_Cu.gbr, SCAN2000_driver-B_Mask.gbr, SCAN2000_driver-B_Paste.gbr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]
2023-06-18 small silkscreen change
    [scan2000_breakout.kicad_pcb]
2023-06-28 Updates after fabrication
    [61202622921.stp, 71922_y26_asm.stp, 72918.stp, SCAN2000_rearconn-Edge_Cuts.gbr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]
2023-06-29 added calibration script
    [results.xlsx]
2023-06-29 Explanation of calibration
2023-06-30 better testing
    [results.xlsx]
2023-08-10 WIP on better calibration
    [results.xlsx]
2023-08-11 better measurement via trigger sync
    [results.xlsx]
2023-08-11 fitting done via solver
    [results.xlsx]
